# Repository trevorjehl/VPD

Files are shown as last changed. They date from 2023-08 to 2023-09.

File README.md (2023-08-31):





Stanford SNF

# Low-Cost Open Source Vapor Phase Decomposition Scanner

This purpose of this project is to create a low-cost vapor phase decomposition droplet scanner for use in semiconductor research labs. 

Scanner_Running_gif

<!-- ## Table of Contents

| Sections      | Description  |
|---------------|--------------|
| [Introduction](#introduction) | - Low-Cost Open Source Vapor Phase Decomposition Scanner<br> - Project Purpose |
| [Rationale](#rationale) | |
| [Download & Installation](#download--installation) | - Download Methods<br> - Python Version<br> - Project Dependencies |
| [Command Line Usage](#command-line-usage) | - Generating G-Code Files<br> - Usage on Ender 3 3D Printer |
| [Modifying The Scan Routine](#modifying-the-scan-routine) | - Custom Scan Documentation<br> - Advanced Modifications<br> - Contribution Guidelines |
| [Project Goals & Next Steps](#project-goals--next-steps) | - Scan Base Redesign<br> - Wafer Piece Scanning<br> - Increasing Scan Droplet Volume<br> - Enclosure Design<br> - Construction & Replication Instructions |
| [Credits](#credits) | - Collaborators<br> - Supervision |
| [License](#license) | - GPL v3 Licensing Information | -->

## Rationale

Although traditional semiconductor manufactureres have access to the large, expensive VPD machines to evaluate silicon wafer contamination, these machines can be innacesible for smaller research facilities.

This project uses a modififed low-cost, open source 3D-printer as the basic platform for the scanner. A custom printehead was designed to hold a 1mL acid-resistant (polypropylene) plastic syringe. This repo contains the neccesary code to program complex scanning sequences for the scanning apparatus.

## Download & Installation

To download the project, copy all project files to your hard drive. This can be done either by downloading the project, cloning the repo, or creating a branch.

- This project runs on Python 3.11.4, so ensure your Python installation is up to date.
- The only dependency for this project is the `math` module.

## Command Line Usage
To create a new G-Code file, use the following command line syntax:

```console
foo@bar:~$ python3 TEMPLATE.py filename.gcode
```

This will create a `.gcode` file in your local directory according to the settings and steps outlined in TEMPLATE.py. To run this easily on the Ender 3 3D printer (or similar), two methods can be used. For testing, software such as Repetier Host can be used, which communicates with 3D Printers over USB.

For more permanent installation, the `.gcode` file can be copied over to the 3D printer's SD/microSD card, which can then be run using the 3D printer's interface

## Modifying The Scan Routine
Refer to [CUSTOM_SCAN.md](/Guides%20&%20Additional%20Documentation/CUSTOM_SCAN.md) for detailed documentation, including various wafer sizes, using cuevettes for dispensing/collecting fluid, changing the location of the cuevette, scan speed, etc.

This project was created with customization in mind, and is therefore easy to modify to suit your needs. For more in-depth changes, consult [USING_TEMPLATE.md](/Guides%20&%20Additional%20Documentation/USING_TEMPLATE.md). 

If you do make changes, please contribute per the standards outlined in [CONTRIBUTING.md](CONTRIBUTING.md). As a reminder, if you release the modified version to the public in some way, the GNU license agreement requires you to make the modified source code available to the program's users.

## Project Goals & Next Steps
- [ ] Complete redesign of scan base to be CNC machined from Teflon/PTFE
- [ ] Add wafer piece scanning functionality (vacuum chuck?).
- [ ] Consider methods of increasing scan droplet volume, as this may aid ICP-MS measurements.
- [ ] Design encolosure/spill area to contain the system and any acid that may spill during operation.
- [ ] Create detailed construction/replication instructions with photos for use in other fabs.

## Credits
This project was made in collaboration with Uriel Valencia. Overseen by [Alexander Denton](https://profiles.stanford.edu/alexander-denton), Stanford Nanofabrication Facility. 

## License

This program is free software: you can redistribute it and/or modify it under the terms of the GNU General Public License as published by the Free Software Foundation, either version 3 of the License, or (at your option) any later version.

For further details, see <https://www.gnu.org/licenses/>.

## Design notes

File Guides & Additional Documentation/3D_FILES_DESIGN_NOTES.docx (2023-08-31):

Uriel Valencia

Stanford Nano Facilities

30 August 2023

Vapor Phase Decomposition (VPD) Machine - Wafer & Cuvette Holder Base, Wafer Holders, and Cuvette Holders

Wafer & Cuvette Holder Base (Original Design - 8/13/23):

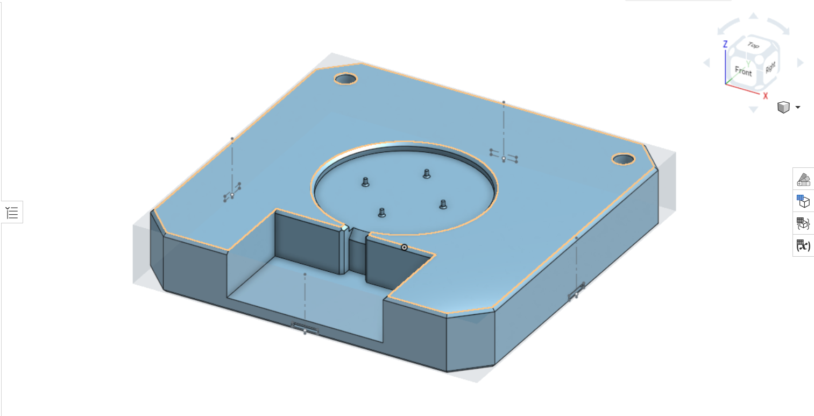
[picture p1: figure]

Figure 1: Wafer & Cuvette Holder Base (Original Design)

The original design for the Wafer & Cuvette Holder Base (to be referred to as “The Base”, from now on) was designed by taking measurements of a Cuvette, a 4” (100 mm) Silicon Wafer, Binder Clips, the bed of an Ender 3 3D Printer, and Wafer Tweezers. Rulers, as well as Calipers, were used to take measurements (in mm).

- The dimensions of The Base were determined by taking the height of a cuvette (40 mm), as well as the length and width of the Ender 3 3D Printer Bed (235 mm x 235 mm). The height of The Base was 38.6 mm, and the length and width were 225 mm x 225 mm after making some adjustments.
- Slots for binder clips were positioned on the Front, Left, Back, and Right sides of The Base. The dimensions for the slots were determined by taking measurements of the binder clips. The dimensions of the binder clip slots were 3 mm high x 16.5 mm wide x 3 mm wide.
- Two cuvette slots were made on the Top face of The Base. The height and diameter of the cuvette slots were determined by taking measurements of a cuvette. The dimensions of the cuvette slots were 38.6 mm deep, with a diameter of 11.5 mm.
- A slot for 4” silicon wafers was made on the Top face of The Base. The diameter of the wafer slot was erroneously determined by assuming that a 4” silicon wafer had a diameter of 101.6 mm. The diameter of the wafer slot was 102.1 mm. Four pegs were included on the bottom of the wafer slot to prevent either side of a silicon wafer from coming in full contact with The Base. The depth of the wafer slot was 5 mm, and the height of the pegs were 4 mm so that, when the silicon wafer was resting on the pegs, the surface of the silicon wafer would be flush with the Top face of The Base.
- A big cut out was placed on the Front face of The Base so that a hand could move with ease when handing wafer tweezers. There is another slot between the big cut out and the wafer slot. The width of the tweezer slot was determined by measuring the width of a wafer tweezer, 12.7 mm wide. The width of the tweezer slot was 14 mm wide. The tweezer slot was made so that any user could place or remove a 4” silicon wafer on the wafer slot.

The following sections will mention what did not work in the original design, the following versions, and what was done to improve on what did not work.

Wafer & Cuvette Holder Base (Original Design - V2 - 8/17/23)

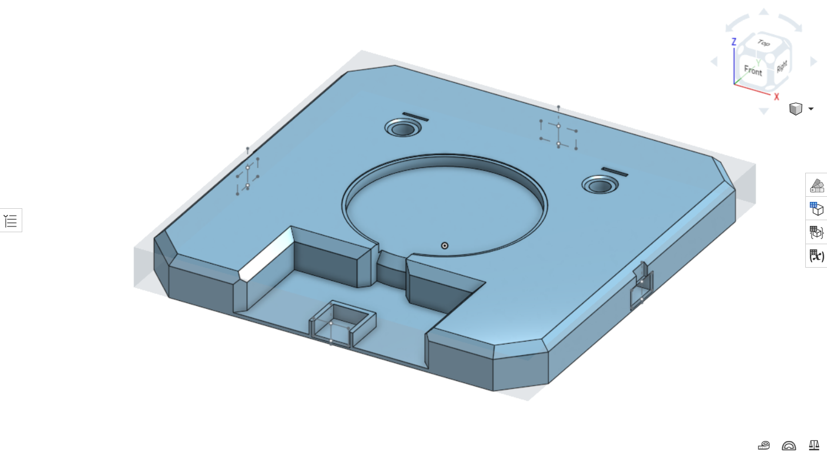
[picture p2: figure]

Figure 2: Wafer & Cuvette Holder Base (Version 2)

- The original design of The Base was too bulky. The length and width dimensions remained the same, but the height was reduced to 23 mm.
- The binder clip slots were not functional; the binder clips could not go into the slot. To fix the problem, the dimensions of the binder clips slots were changed to: 10 mm high x 20 mm wide x 20 mm long. This gave the binder clips enough clearance to go into the binder clip slots. An additional was made above the binder clip slots so that the handles of the binder clips could rest on them so the handles would not interfere with the bed of the Ender 3 3D printer when it moves in the y- direction.
- The two cuvette slots where the cuvettes would be placed in were too snug; force was needed to put in, and remove, the cuvettes from the circular slots. To fix this, the diameter was increased to 11 mm. The depth changed to 23 mm since the height of The Base was reduced to 23 mm. Additionally, there was an issue with repeatability; there was no way to prevent the cuvettes from moving in a circular motion while in the cuvette slots. To prevent the cuvettes from moving, slots for the caps of the cuvettes were made near the cuvette slots to hold the cuvettes in place. The dimensions of the cap slots were 1.6 mm long x 14 mm wide x 23 mm deep.
- The diameter of the wafer slot was too big. The diameter of the wafer slot was reduced to 101.86 mm. Also, the silicon wafer was not stable when placed on the pegs. Applying force to certain areas, like closer to the edge of the silicon wafer, would cause the silicon wafer to tilt. To fix this, the pegs were removed, and a ring that was 1mm lower than the wafer slot was used instead. The wafer ring was 98 mm in diameter.
- The wafer tweezer slot was too narrow; there was no room for the wafer tweezers to move sideways when placing or removing a silicon wafer. To fix this, the width of the wafer tweezer slot was increased to 20 mm.

Wafer & Cuvette Holder Base (Original Design - V3 - 8/18/23)

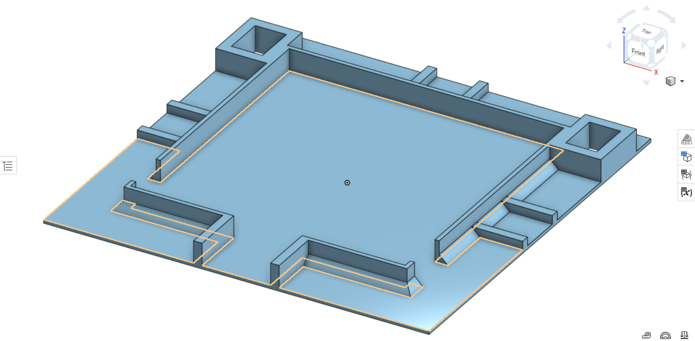
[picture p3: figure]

Figure 3: Wafer & Cuvette Holder Base (Version 3)

In this version of The Base, the wafer slot holder was removed. Since silicon wafers come in different diameters, 51 mm, 100 mm, and 150 mm, it was decided that a larger, rectangular slot, should be made so that three different wafer holders could be made, and therefore interchangeable. Also, the cuvette slots were removed, as well as the cap slots, in favor of cuvette holder slots, where cuvette holders could be inserted into the slots.

- The length and base of The Base remained the same. However, the height was reduced to 15 mm, but this was not applied to the entirety of The Base. The walls of the new wafer holder slots, as well as the cuvette holder slots, were elevated 13 mm high from the base, which was elevated 2 mm high.
- The width of the binder clip slots was increased to 25 mm. The length was increased to 29.85 mm so that the walls on either side of the binder clip slots would act as support for the walls of the wafer holder slot. The walls on either side of the binder clip slots were 5 mm wide, with a height of 5 mm.
- The cuvette slots, and cap slots, were removed and replaced with cuvette holder slots (cuvette holder slots will be talked about later). The external perimeter dimensions of the cuvette holder slots were 35.85 mm long, 29.85 mm wide, and 13 mm high. The internal perimeter dimensions of the cuvette holder slot were 24.2 mm wide, 18.2 mm wide, and 15 mm deep.
- The wafer slot was replaced with the wafer holder slot. The external perimeter dimensions of the wafer holder slot were 165.3 mm long and wide, with a height of 13 mm. The internal perimeter dimensions of the wafer holder slot were 160.3 mm long and wide, with a depth of 15 mm. Wafer holders will be talked about later.
- The big cut out from Version 1, and the wafer tweezer slot, became one. The new wafer tweezer slot was 40 mm wide and 29.85 mm long. The walls next to the wafer tweezer slot were 5 mm wide, 29.85 mm long, and 13 mm high.
- Cut outs were made on the Left and Right faces of the wafer holder slot. The cut outs were 8 mm long, 25 mm wide, and 13 mm high.

Wafer & Cuvette Holder Base (Final Version - 8/29/23)

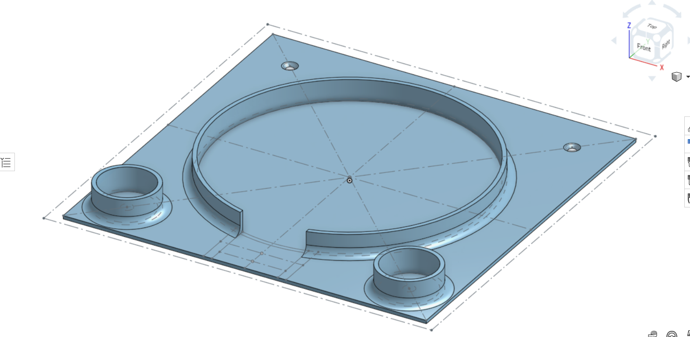
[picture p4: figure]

Figure 4: Wafer & Cuvette Holder Base (Final Version)

For the Final Version, the binder clip slots from previous iterations were removed, and instead replaced with holes so that The Base would be bolted on to the bed of the Ender 3 3D Printer. Also, the wafer holder slot, and the cuvette holder slots, were redesigned to be round, as opposed to square or rectangular. This design is better for when The Base gets manufactured.

- The length and width of The Base was reduced to 220 mm x 220 mm. This was done so that the length and width of The Base was within the effective printing area of the Ender 3D printer. Overall height of The base is 15 mm. The base is 2mm high, and the height of the wafer and cuvette holder slots are 13mm high.
- The binder clip slots were removed in favor of counter sink, standard M4 holes. The advantage to the counter sink holes is that the screws of the levels (on the bottom of the Ender 3 3D Printer bed) can be used to fasten the The Base onto the Ender 3D Printer bed.
- The previous cuvette holder slots were redesigned to be round. Easier to manufacture. The cuvette holder slots were moved from the back of the Top face to the front. Also, the two cuvette holder slots are located where two of the counter sink holes are located; the counter sink holes will not interfere with the cuvette holders.
- The wafer holder slot was redesigned to be round; easier to manufacture. The cut outs to remove the interchangeable wafer holders were removed. Instead, the cut outs were made on the bottom of the wafer holder, which can be accessed from the wafer tweezer slot.
- The walls next to the wafer tweezer slot area were removed, as they were unnecessary at this point. The width of the wafer tweezer slot remained the same.

Rectangular Cuvette Holder (Original Version - ~ 8/15/23)

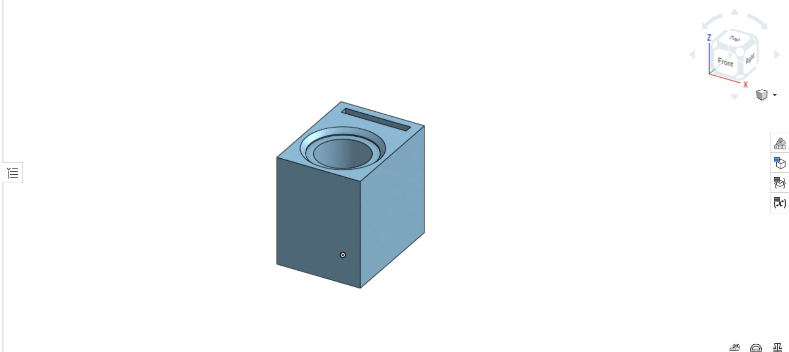
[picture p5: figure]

Figure 5: Rectangular Cuvette Holder (Original Design)

This Rectangular Cuvette Holder (to be referred as “The Cuvette Holder” from now on) was made during V3 of The Base was being designed.

- The cuvette Holder is 24 mm long x 18 mm wide, with a height of 23 mm. The height of The Cuvette Holder was intentionally higher than the cuvette holder slot on The Base so that The Cuvette Holder could be easily placed and removed.
- The diameter of the slot where the cuvette goes in is 11 mm, and it is 23 mm deep (from Top face to the Bottom face. The cap slot is 1.7 mm long and 14 mm wide, with a depth of 23 mm.
- The lip of the cuvette does not rest on the Top face of The Cuvette Holder. The Cuvette Holder is intentionally shorter than the cuvette so that the cuvette can be easily placed and removed from the cuvette slot.

Round Cuvette Holder (Final Version - 8/29/23)

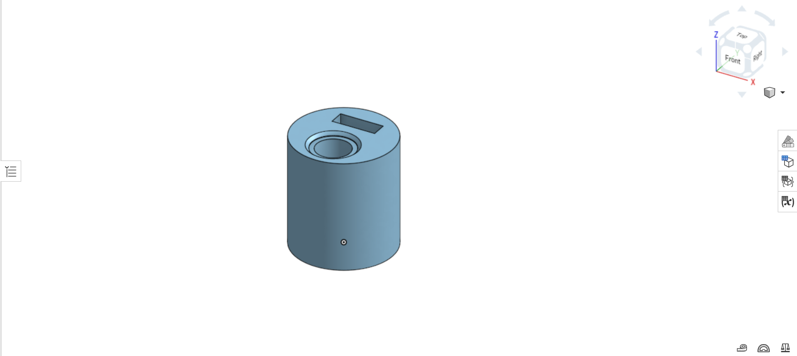
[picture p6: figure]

Figure 6: Round Cuvette Holder (Final Version)

The (Round) Cuvette Holder was made when the Final Version of The Base was being designed.

- The Cuvette Holder was redesigned to be round so it would fit in the circular cuvette holder slots in the Final Version of The Base. The diameter of The Cuvette Holder is 32 mm, and its height was increased to 35 mm so that the cuvette would have less room to move around.
- The diameter of the cuvette slot was reduced to 10.9 mm so that the cuvette would move around less. The depth of both the cuvette slot, and the cap slot, was increased to 35 mm. The length of the cap slot was increased to 4.9 mm so that more of the cap would fit in the slot.

Wafer Holder (Original Version - 8/21/23)

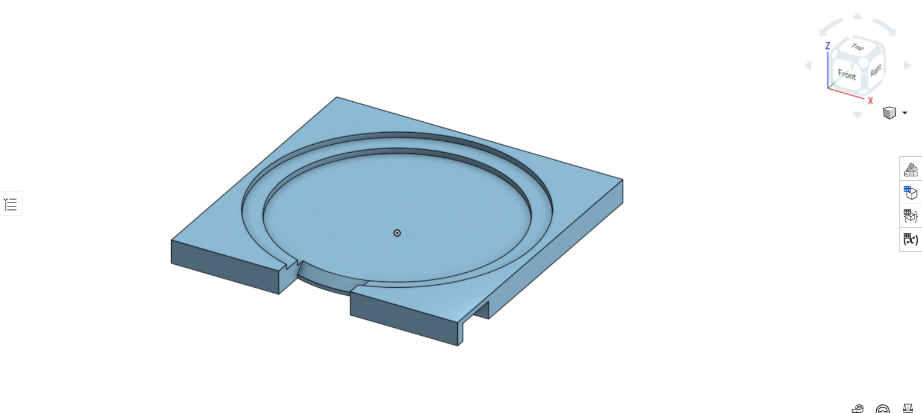
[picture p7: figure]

Figure 7: 6” Wafer Holder (Original Version)

The Wafer Holders (of sizes 51 mm, 100 mm, and 150 mm) were designed when V3 of The Base was being designed. The idea was to create three separate wafer holders, for each size of silicon wafer, so that they could be interchangeable with V3 of The Base.

- The dimensions of the wafer holder (for all three sizes) were 160 mm long x 160 mm wide, with a height of 13 mm.
- The difference between the three wafer holders are the diameters of the wafer slots, as well as the wafer rings the silicon wafers rest on. The 6” Wafer Holder (Figure 7) has a wafer slot diameter of 150.6 mm, and a wafer ring diameter of 130 mm. For the 4” Wafer Holder, the wafer slot diameter was 100.6 mm, with a wafer ring diameter of 80 mm. For the 2” Wafer Holder, the wafer slot diameter was 51.6 mm,and the wafer ring diameter was 30 mm.
- The wafer tweezer slot remained the same; 40 mm wide.
- Slots to remove and place the wafer holder from The Base were placed on the Left and Right faces of the wafer holders. The slots were 20 mm long by 25 mm wide, with a height of 10 mm.

Wafer Holder (Final version - 8/29/23)

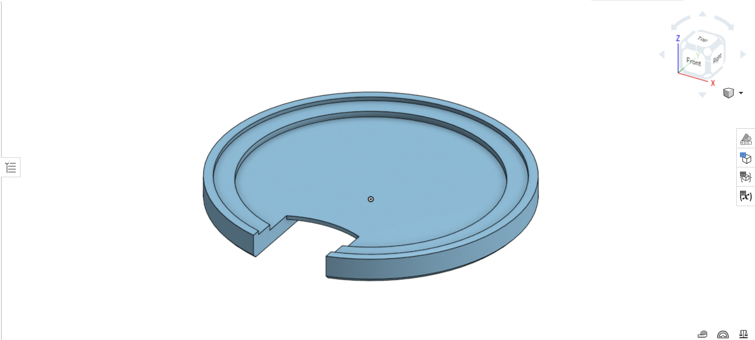
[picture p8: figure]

Figure 8: 6” Wafer Holder (Final Version)

The Final version of the wafer holders (51 mm, 100 mm, and 150 mm) were redesigned so that they would fit the Final Version of The Base.

- The wafer holders were redesigned to be circular so that they would fit the circular wafer slots of the Final Version of The Base. All three wafer holders had a diameter of 160 mm. Diameters for the wafer slots, as well as the wafer rings, remained the same.
- The width of the wafer tweezer slot remained unchanged.
- The slots to place and remove the wafer holders from The Base were removed from the, and instead a slot was created under the wafer tweezer slot. For all three wafer holders, the dimensions of the slot to place and remove the wafer holder are 25 mm long x 40 mm wide, with a height of 6 mm.

VPD Machine

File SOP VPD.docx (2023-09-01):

Document: Vapor Phase Decomposition Droplet Scanner Standard Operating Procedure | Revision: A | Release Date:

Prepared by: Trevor Jehl

Table of Contents

# 1. Equipment Purpose

  1.1. The VPD droplet scanner is designed to use an acidic scanning solution to extract contaminants from a silicon wafer so that the contaminants may later be measured through use of an ICP-MS.

# 2. Equipment Specifications

# 3. Cleanliness Standard

  3.1. TBD

# 4. Processing Capabilities

# 5. Becoming a User

# 6. Safety

  6.1. This device uses an acidic scanning solution that contains HF. Ensure that all proper protocols are followed for acid & HF handling. If the contact is made with HF, immediately stop using the machine follow the necessary procedure for an HF spill.
  6.2. This device has open, moving wires. Before use, ensure that all wires are free to move and that they will not cause damage when the machine is in motion.
  6.3. This machine has multiple cooling ducts and fan systems to ensure proper cooling of all electronic components.
    6.3.1. Ensure that each cooling duct is not blocked before using the machine.
    6.3.2. If liquid of any kind, including the scanning liquid, comes in contact with the metal frame of the machine, immediately turn off power to the machine and unplug it from all outlets. Ensure that the spill is properly reported and handled. Before resuming use, ensure that all electronic components are free from moisture and corrosion.
  6.4. During and following use, the machine’s motors will become hot to the touch. Take precautions to ensure that this heat does not cause harm to the user or to lab equipment.

# 7. Required Equipment

  7.1. 4 or 6 inch silicon wafer. Wafer pieces are not able to be processed at this time.
  7.2. Appropriate size wafer holder for the wafer being scanned.
  7.3. Sanitized 1mL polypropylene plastic syringe.
  7.4. Sanitized cuvette for storage of sample droplet.
  7.5. Pre-mixed scanning solution.

# 8. Operating Procedure

Before beginning, familiarize yourself with the safety considerations outlined in section 6.

  8.1. If the scan head is not in the back left corner of the scan plate, follow abort procedure (section 13) to avoid damaging the machine.
  8.2. Perform an overall inspection of the machine. Ensure that all wires are free to move and will not catch during machine operation. Ensure that all air ducts are free from debris and moisture. Ensure that the scan motor cable is properly seated in the scan motor cable guide.
  8.3. Align the syringe plunger holder with the zero mark on the syringe, either by using the provided alignment mark on the side of the scan head or by inserting a syringe into the head, depressing the plunger holder as much as possible, and carefully removing the syringe to avoid moving the plunger holder.
  8.4. Find the correct size wafer holder for your sample and insert it into the scan base, making sure that the slot in the wafer holder aligns with the corresponding slot on the scan base. Carefully insert your wafer into the slot in the wafer holder.
  8.5. Turn the machine on using the red switch on the right side of the machine. Depress the selection wheel to access the menu items. Rotate the wheel to select “Print from Media.” Depress the wheel again to select.
  8.6. Rotate the selection wheel to find the appropriate scan routine for your wafer (e.g. for a 4 inch wafer, select “4inScan.gcode”). Depress the wheel and select “Print” to begin the scan.
  8.7. After automatic calibration, the scanner will place the scan head over the wafer, open the plunger holder, and beep. Fill your sanitized syringe with the appropriate amount of scan solution (see section 11), and place it into the slot in the scan head, making sure that the plunger is securely seated in the plunger holder. Once finished, depress the selection dial to begin your scan.
  8.8. The scanner will begin the scan routine. At the end of the cycle, it will collect the scan droplet, fully open the syringe plunger holder for easy removal, and emit an audible beep.
  8.9. Once the cycle has finished and the scanner has beeped, remove the syringe from the plunger, making sure not to spill any solution from the syringe. Dispense your sample into the appropriate cuvette and seal it. Press the selection dial once more to finish the cycle. Dispose of the syringe appropriately.
  8.10. Depress the selection dial, which will move the plunger holder to the “0” mark and move to the scan head to the back left of the scan plate. Turn the machine off using the red switch on the right side of the machine.
  8.11. Remove the wafer with wafer with wafer tweezers.
  8.12. If any solution spilled during the procedure, clean all affected parts thoroughly.
9. Recipe Parameters
  9.1. Scan Solution:

# 10. Definitions and Process Terminology

  10.1. Bed Leveling Knobs: The bed leveling knobs are positioned at the four corners of the scan plate. They serve to adjust the compression of the scan plate spacers.
  10.2. Cuvette Holder: Small, cylindrical plastic piece that can be inserted into the scan base. The cuvette holder has a hole through its center so that the cuvette may be inserted into it.
  10.3. Cuvette: A clear plastic container for holding the scan droplet.
  10.4. End Stop: Physical switches on the X & Y axes that tell the system where the ends of the
  10.5. ICP-MS: Inductively coupled plasma mass spectrometry. The technique used to quantify the composition of contaminants in the scan droplet.
  10.6. Interface Screen: The LCD panel at the bottom right of the machine. Used to interact with the machine and select a scanning protocol.
  10.7. Pinion Gear: The plastic gear mounted to the front side of the scan head. It is responsible for transferring the rotational motion of the scan motor to the plunger holder.
  10.8. Plunger Holder: The long, sliding plastic component that wraps around the end of the syringe’s plunger so that it may be moved up and down via the pinion gear and scan motor.
  10.9. Scan Base: The large plastic piece that is mounted to the scan plate and has cylindrical holes for the cuvette holders(s) and wafer holder.
  10.10. Scan Droplet: The small volume of scan solution dragged by the syringe which dissolves and collects wafer contaminants.
  10.11. Scan Head: The plastic assembly bolted to the x-axis gantry. The scan head is connected to the syringe, plunger holder, scan motor, and pinion gear.
  10.12. Scan Motor Wire Guide: This white plastic guide is attached to the top Delrin roller wheel on the left side of the x-axis gantry. It ensures that the scan motor does not become tangled, caught, or otherwise damaged as the scan head moves.
  10.13. Scan Motor: The silver and black rectangular prism bolted into the scan head. This motor is responsible for moving the syringe’s plunger by moving the pinion gear.
  10.14. Scan Plate Spacers: Four cylinders with holes through their center points for countersunk bolts. These spacers keep the scan plate even and level across it’s face.
  10.15. Scan Plate: The large square metal base that the scan base is bolted to.
  10.16. Scan Solution: The acidic solution that makes up the scan droplet. This solution is used to dissolve contaminants in the wafer.
  10.17. Selection Dial: The round knob at the bottom right below the interface screen.
  10.18. Syringe: This system is designed to use 1mL HSW® Norm-Ject® Luer-Slip Syringes, Air-Tite. This syringe press fits into the scan head, and the syringe plunger fits into the plunger holder. They can be easily identified by their blue-green plunger and clear main body.
  10.19. VPD: Vapor phase decomposition, an established technique for contamination analysis of wafers.
  10.20. Wafer Holder: Cylindrical insert for the scan plate upon which the silicon wafer to be scanned rests.

# 11. Process Data

  11.1. 4-inch (100mm) Wafer
    11.1.1. Scan Duration: ~20 minutes.
    11.1.2. Scan Radius: From radius 65.0mm to 5.0mm
    11.1.3. Scan Droplet Volume: 0.05mL
  11.2. 6-inch (150mm) Wafer
    11.2.1. Scan Duration: ~53 minutes.
    11.2.2. Scan Area: From radius 40.0 to 4.0.
    11.2.3. Scan Droplet Volume: 0.05mL

# 12. Troubleshooting

Symptom | Issue | Resolution
The loaded syringe won’t fit into the scan head. | Failure to align the plunger holder before scan. | Turn the machine off. Align the mark on the plunger holder with the mark on the scan head body. Alternatively, place the syringe with the plunger fully depressed into the scan head. Once the plunger is fully aligned at 0mL, remove the syringe. Be careful not to move the plunger holder.
The printer won’t move after starting a scan routine or after instructing printer to move | Disconnected wires | Ensure that all four (4) motor wires are fully connected. Ensure that all three (3) end stop cables are fully connected. Cables are labeled for convenience with yellow tags at the cable ends.
There are no files under “Print from Media” | SD read error or disconnected SD card | Above “Print from Media,” press “Change Media” to re-read the SD card. Recheck “Print from Media.” If there are still no visible files, turn off the scanner. Unplug the microSD card from the front of the scanner, remove it, and replace it. Ensure that it fully ‘clicks’ in. Recheck “Print from Media.”
The scan droplet is consistently lost in the same spot on the wafer | Uneven scan surface. | First, ensure that the wafer holder is fully seated and flat in the scan base. Verify that the syringe is fully seated in the scan head. If problems persist, verify the adjustment of the eccentric nuts, particularly on the scan head and y-axis. If issues continue, level the system by following the leveling procedure outlines in “Maintenance”
The system won’t turn on. | Loose power cable. | Over time, the power cable can become loose. Make sure the red switch is set to off (O) before checking that both the system side and wall socke side of the power cable is fully seated.

# 13. Abort Procedure

If, for any reason, the machine must be interrupted during a regular scan cycle, follow this procedure to prevent damage to the system.

  13.1. Turn the machine off using the red power switch on the right side of the machine. Then, unplug the power cord.
  13.2. Clean up any scanning solution that may be left behind. Remove the syringe from the scan head.
  13.3. Move the syringe plunger holder down to the zero point. You will be unable to do this after the machine is powered on.
  13.4. Once the system has been cleaned, ensure that the red switch is in the OFF (O) position before plugging in the power cable. Once the cable is fully seated, you may turn the system on.
  13.5. Finally, it is important to ensure that the printhead will not encounter any obstacles when running the next scan procedure. To do so, use the machine’s interface (Press knob > Motion > Move Axis > Move Z > Move 10mm > Rotate knob to move) to raise the Z-axis well above any obstacles on the XY plane.

# 14. Maintenance

To ensure smooth operation of the system, a few regular maintenance items should be conducted. This section will divide these maintenance items by the frequency that they should be performed.

Before performing any maintenance, ensure that the machine has been turned off and is unplugged unless otherwise noted.

  14.1. XY Belts
    14.1.1. Belt Tension: The X & Y belts of the system help maintain the dimensional consistency of the scanner. Over time, these belts will loosen and the machine’s ability to move in the XY plane will be hampered. To tighten the belts
      14.1.1.1. Locate and access the belt tensioner at one end of the axis on which you want to tighten the belt.
      14.1.1.2. Use the appropriate Allen key to loosen the belt tensioner. There are two screws on the X-axis and four on the Y-axis of the machine.
      14.1.1.3. Once the tensioner is loose on the frame, hold the frame with one hand and with moderate strength pull the tensioner in the direction that will tighten the belts (away from the moving part).
      14.1.1.4. Hold the tensioner in its far-back position, let go of the frame, and, using the Allen key used earlier, tighten the bolts so that the tensioner is tight. Do not overtighten these bolts.
      14.1.1.5. After tensioning the system, perform a visual inspection of the T-nuts behind the bolts. Ensure that they are facing upwards, perpendicular to the length of the metal frame. If they are not, the nut will not be secured against the frame and the belt will quietly lose tension. See (15.2) for a visual guide to proper installation.
    14.1.2. Belts are a consumable part. After extended periods of use, they will show signs of wear (cracking, tearing, fraying). Replace and reattach belts as needed. Follow the above procedure to ensure proper belt tension.
  14.2. Delrin V-Slot Wheels
    14.2.1. The moving axes of this printer connect to the frame via rolling Delrin wheels.
      14.2.1.1. Each side of the x-axis gantry has three (3) wheels. The scan head has another three (3) wheels. Below the moving y-axis plate are four (4) additional wheels.
    14.2.2. If scan head wobble, grinding, skipping, excess wear, inaccurate XY motion (after ensuring proper belt tension) Wheel tightness to the frame can be adjusted using the eccentric nuts on the machine. Each side of the x-axis gantry has one (1) eccentric nut on the inside rolling wheel. The scan head has one (1) nut on the bottom wheel. The right side of the rolling y-axis gantry has two (2) eccentric nuts. These nuts can be identified by their larger size and hexagonal shape. See (15.1) for a photo example. To adjust the nuts:
      14.2.2.1. Obtain the proper size wrench (10mm).
      14.2.2.2. Identify the axis and eccentric nut that need to be adjusted.
      14.2.2.3. Using the wrench, rotate the nut. To check tightness, hold the axis in place and attempt to rotate the Delrin wheel. The wheel should rotate in place with a slight amount of force needed to keep the axis in place.
      14.2.2.4. Once you are satisfied with the ability of the wheel to rotate, check the other wheels of the axis as they will have been affected by this adjustment.
      14.2.2.5. Finally, verify overall axis motion. The axis should move freely without excess resistance but should be tight enough to be free of wobble, tilt, or rotation.
    14.2.3. These wheels are consumable and will wear over time. Symptoms of worn wheels include visible wear on axes and frame of printer, sagging x-axis gantry, inconsistent or inaccurate axis motion, or significant differences noted in the size or shape of one of the wheels. Before replacing wheels, ensure that the eccentric nuts have been adjusted properly.
  14.3. Z-Axis Threaded Rod
    14.3.1. The Z-axis threaded rod is located behind the left vertical frame of the machine. It is responsible for powering the vertical movement of the scan head.
    14.3.2. Since the rod has metal-on-metal contact, it will require periodic lubrication to prevent excess wear. To lubricate the axis:
      14.3.2.1. Remove any old lubricant by thoroughly cleaning the rod using isopropyl alcohol. Use the machine’s controls (Press knob > Motion > Move Axis > Move Z > Move 10mm > Rotate knob to move) to spin and move the axis for thorough cleaning. Be careful not to raise the Z-axis too high to prevent snagging or catching of wires.
      14.3.2.2. Apply an appropriate amount of lubricant to the length of the rod. Use the machine again to move the axis up and down multiple times to ensure even distribution across the rod.
      14.3.2.3. If using non-Teflon lubricant, wipe off excess lubricant to leave behind only a thin layer.
  14.4. Scan Plate & Scan Plate Springs
    14.4.1. Currently, the system uses springs to level the scan plate, which in turn levels the scan bed, the wafer holder and wafer. Ensuring that the scan plate is level relative to the syringe tip is essential for reliable operation of the system. If the plate is not level, the distance from the syringe tip to the wafer will vary across the scan, and the tip may lose contact with the drop or dig into the wafer or wafer holder. To level the scan plate:

(Note: Be advised that if the bed is particularly poorly leveled at the start of this process, the syringe tip may grind and press into the wafer holder plate. If there is concern that this may be an issue, tighten all four (4) knobs down before beginning the scanning process).

      14.4.1.1. Obtain either a 0.1mm feeler gauge or a blank piece of printer paper. You will also need a syringe and the 4in wafer holder. Insert the wafer holder into the scan base.
      14.4.1.2. Navigate to the “Print from media” menu on the scanner and select “levelScanner.gcode” The scanner will automatically calibrate before moving to the center of the wafer holder. After the beep, insert the syringe and press the selection dial to begin the leveling process.
      14.4.1.3. The syringe tip will lower down to Z = 0. In sequence, the syringe tip will be slowly moved towards the four corners of the scan plate. The user will level each point, then the system will return to each point to check that the level was executed properly.
      14.4.1.4. To level a point, slide the feeler gauge or portion of paper underneath the tip of the syringe. Adjust the respective leveling knob so that there is a slight amount of resistance when moving the gauge or paper. Remember that that when looking straight down over the scanner, rotating the knobs clockwise will tighten them, increasing the gap between the syringe and surface. To decrease the distance, turn the knobs counterclockwise.
      14.4.1.5. Once you are satisfied with the point, press the selection knob to move to the next point.
      14.4.1.6. After you have leveled and re-leveled all four points, the scan holder will open the plunger for easy removal of the syringe. Remove the syringe and press the selection knob. Your leveling is now complete.
  14.5. Scan Head (Syringe Holder, Plunger Holder, Pinion Gear, Scan Motor)
    14.5.1. The plunger holder should not need regular maintenance or replacement.
    14.5.2. Periodically check the rack gears on the plunger holder for degradation with use. If wear is noted, replace with a new plunger holder.
    14.5.3. The pinion gear may wear with time. If any wear is noted, remove the gear, and replace with a new gear. To check for wear:
      14.5.3.1. Remove the syringe plunger holder and inspect the gear teeth. They should be straight, with no crushing, warping, twists, or other defects.
      14.5.3.2. To check the connection between the pinion gear and scan motor, run a scan cycle. Observe the interface between shaft of the scan motor and the pinion gear. If there is slipping between the two surfaces, the gear is worn and should be replaced.
    14.5.4. Periodically check all screws and bolts for proper fit and tightness. If bolts are loose, tighten them to finger tightness. Do not over tighten.
    14.5.5. Periodically check the scan motor cable for wear, with particular emphasis on the bottom portion of the cable, as it comes in contact with the scan motor wire holder during scanning. Replace as needed.

# 15. Appendices, Figures & Schematics

  15.1. Y-Axis Eccentric Nut

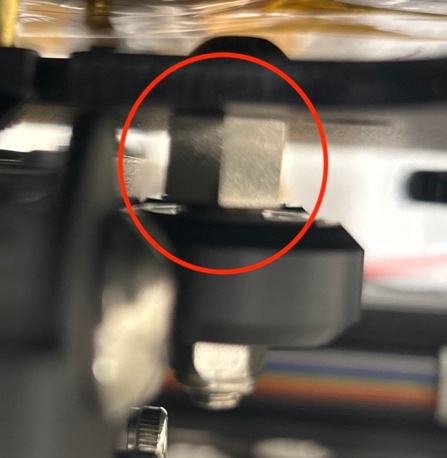
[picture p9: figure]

  15.2. T-Nut Proper & Improper Installation
    15.2.1. Proper T-Nut Installation

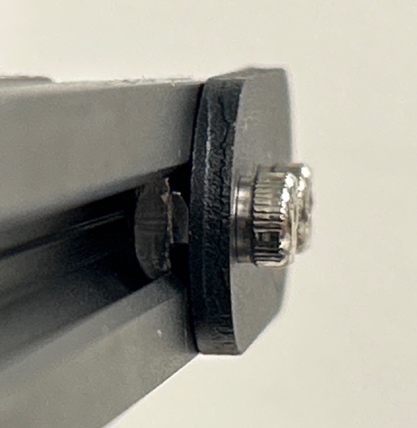
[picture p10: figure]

    15.2.2. Improper T-Nut Installation

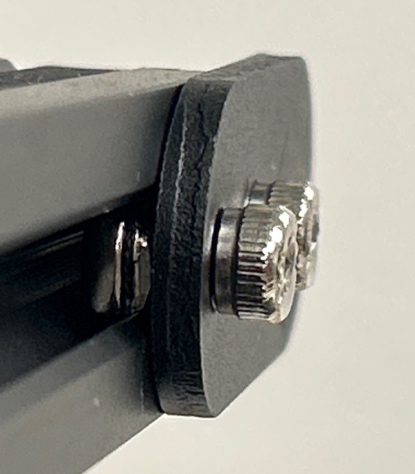
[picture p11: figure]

# 16. Revision Block

Revision | Date | Description of Change | Author
1 | 8/31/23 | Initial creation of SOP. | Trevor Jehl

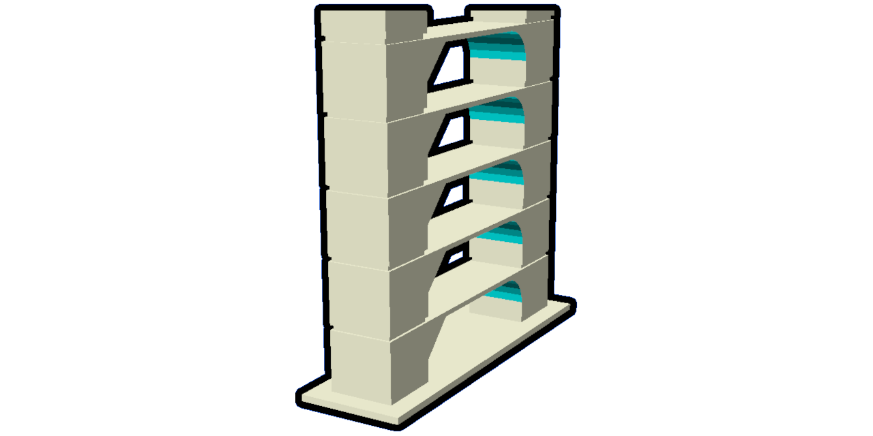
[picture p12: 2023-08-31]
Ender 5 Cura Config/5.4/plugins/AutoTowersGenerator/AutoTowersGenerator/Resources/Images/github_image.png

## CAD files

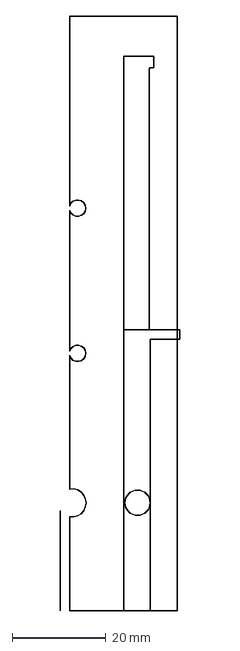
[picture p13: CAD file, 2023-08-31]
CAD FIles/3mL Plastic Syringe Head v15/Syringe Head 1_f84ff1b6/Syringe Holder 1_7d3c671d/Main Syringe Revolve.dxf
25.5 x 127.0 mm

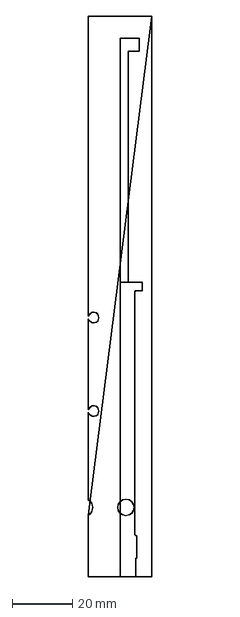
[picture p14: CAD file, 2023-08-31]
CAD FIles/Depracated/7.10.23(morePrintable) v3/Syringe Holder 1_7d3c671d/Main Syringe Revolve.dxf
20.9 x 186.0 mm

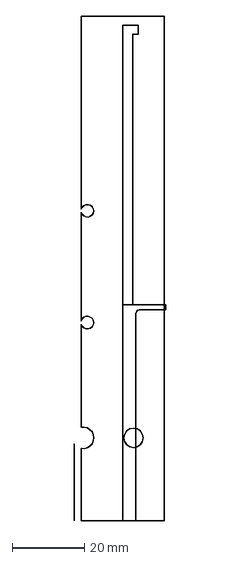
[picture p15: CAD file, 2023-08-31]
CAD FIles/1mL Plastic Syringe Head v13/Syringe Head 1_f84ff1b6/Syringe Holder 1_7d3c671d/Main Syringe Revolve.dxf
25.5 x 140.0 mm

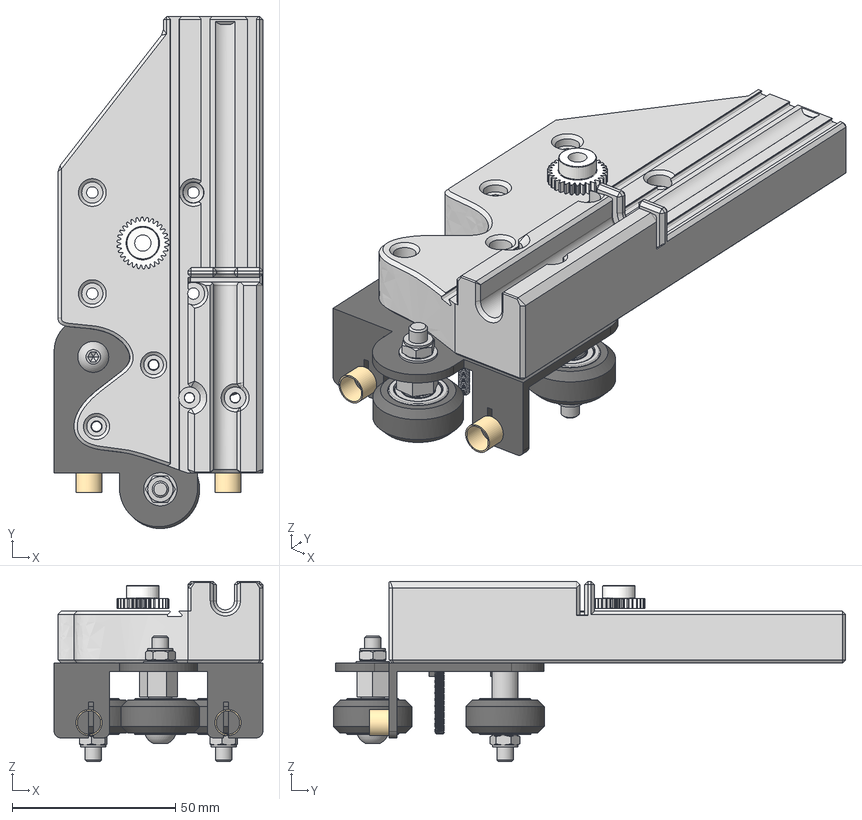
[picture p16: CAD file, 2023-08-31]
CAD FIles/1mL Plastic Syringe Head v13/1mL Plastic Syringe Head_v13.step
64.1 x 157.1 x 55.3 mm
M5X30 Pan Head Screw x 3
M5 Self-locking nut x 3
Rollers x 3
M5 washer1 x 3
625pillow x 6
Eccentric column
M5 washer
Spacers for rollers x 2
Copper Covers x 2
Metal Mounting Bracket
Syringe Holder
20 Degree Pressure Angle Plastic Gear v1 (1)
92095A185_Button Head Hex Drive Screw

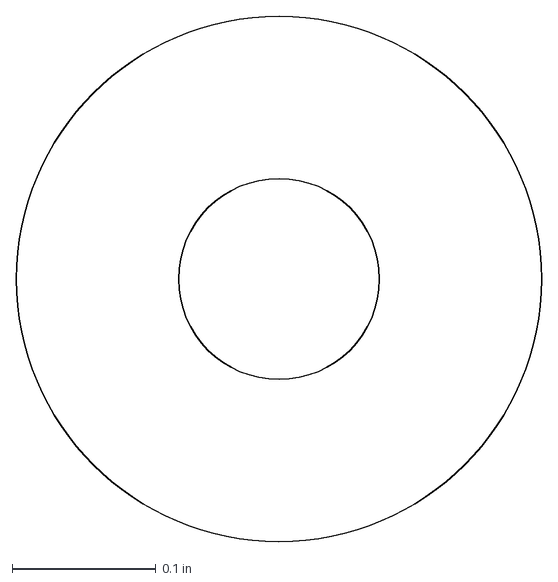
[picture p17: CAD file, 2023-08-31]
CAD FIles/1mL Plastic Syringe Head v13/Syringe Head 1_f84ff1b6/1mL Glass Syringe v18 1_c14a9fbb/Plunger 1_b5b81f4f/Sketch1.dxf
0.366 x 0.366 in

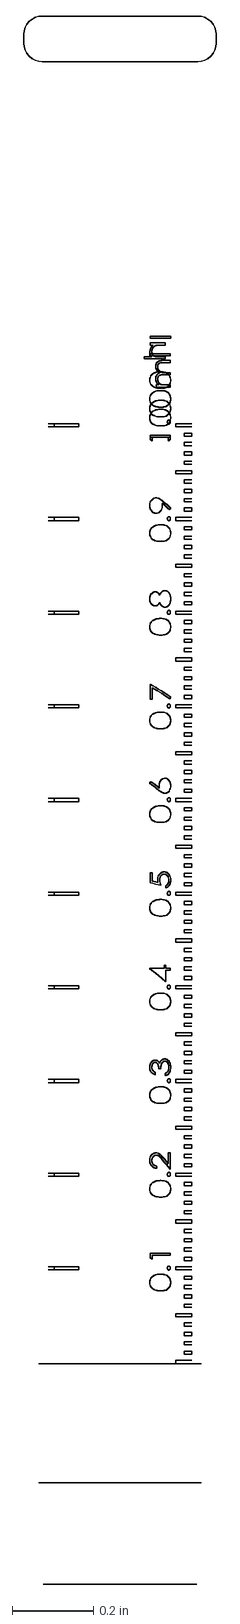
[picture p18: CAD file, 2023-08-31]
CAD FIles/1mL Plastic Syringe Head v13/Syringe Head 1_f84ff1b6/1mL Glass Syringe v18 1_c14a9fbb/Sketch1.dxf
0.472 x 3.85 in

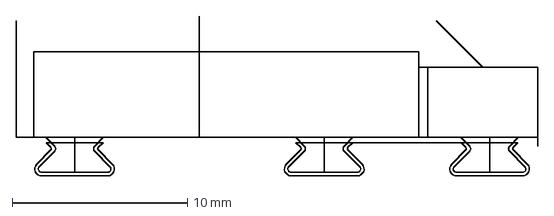
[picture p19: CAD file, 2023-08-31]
CAD FIles/1mL Plastic Syringe Head v13/Syringe Head 1_f84ff1b6/Plunger Holder 1_a4f4313b/Plunger Holder Tracks.dxf
29.8 x 9.14 mm

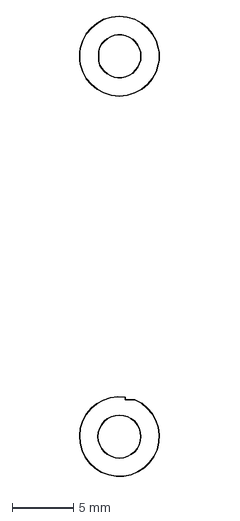
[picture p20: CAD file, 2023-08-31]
CAD FIles/1mL Plastic Syringe Head v13/Syringe Head 1_f84ff1b6/Syringe Holder 1_7d3c671d/Sketch7.dxf
7.17 x 37.8 mm

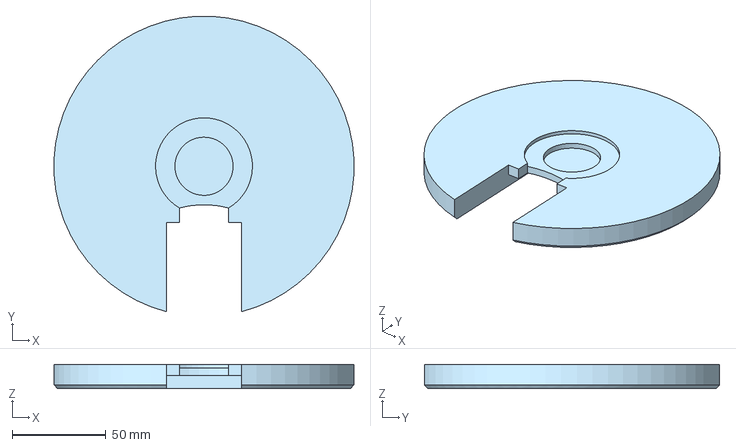
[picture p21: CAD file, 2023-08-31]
CAD FIles/2_ Wafer Holder/[Final] 2_ Wafer Holder (W- Tolerance, 8-29-23).step
159.8 x 157.3 x 13.0 mm

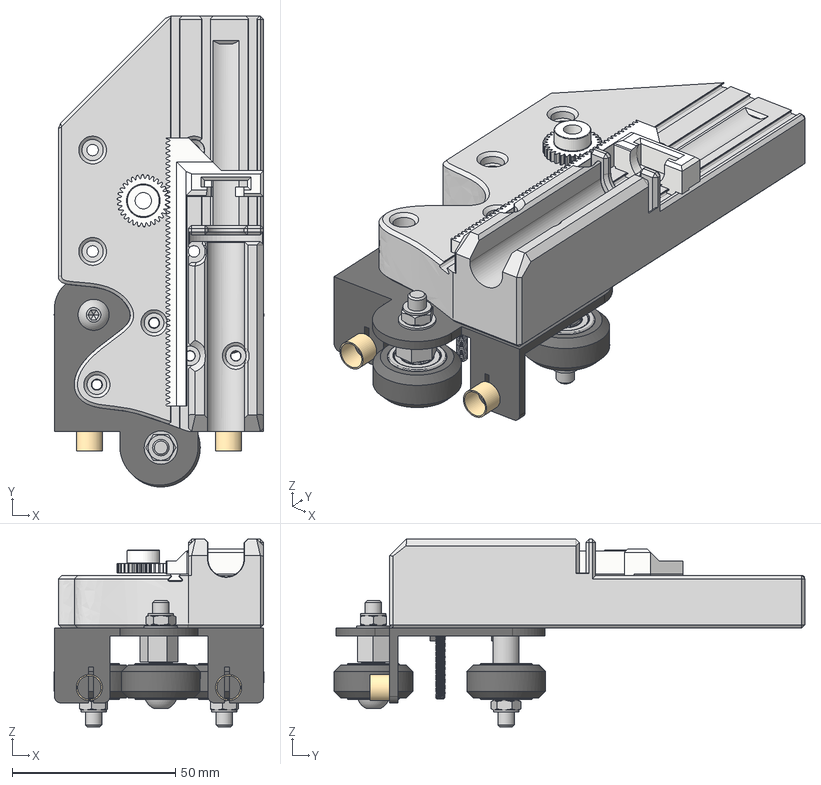
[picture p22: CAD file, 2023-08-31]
CAD FIles/3mL Plastic Syringe Head v15/3mL Plastic Syringe Head_v15.step
64.1 x 144.1 x 57.4 mm
M5X30 Pan Head Screw x 3
M5 Self-locking nut x 3
Rollers x 3
M5 washer1 x 3
625pillow x 6
Eccentric column
M5 washer
Spacers for rollers x 2
Copper Covers x 2
Metal Mounting Bracket
Syringe Holder
20 Degree Pressure Angle Gear Rack v1
20 Degree Pressure Angle Plastic Gear v1 (1)
92095A185_Button Head Hex Drive Screw

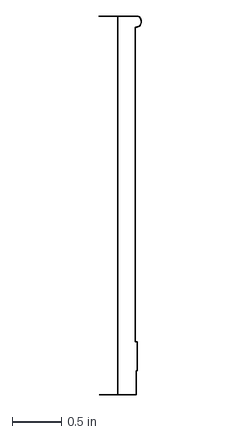
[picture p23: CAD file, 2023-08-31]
CAD FIles/3mL Plastic Syringe Head v15/Syringe Head 1_f84ff1b6/1mL Glass Syringe v18 1_c14a9fbb/Sketch3.dxf
0.427 x 3.85 in

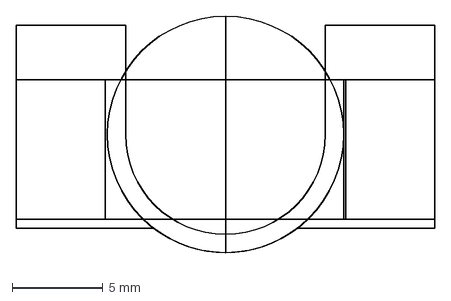
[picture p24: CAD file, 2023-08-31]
CAD FIles/3mL Plastic Syringe Head v15/Syringe Head 1_f84ff1b6/Plunger Holder 1_a4f4313b/Plunger Holder.dxf
23.0 x 13.4 mm

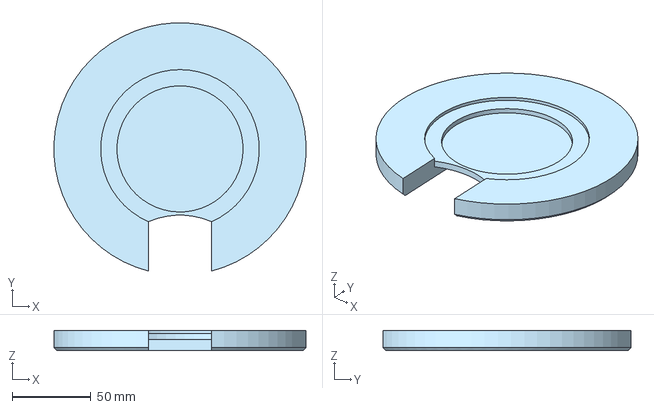
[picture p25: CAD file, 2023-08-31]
CAD FIles/4_ Wafer Holder/[Final] 4_ Wafer Holder (W- Tolerance, 8-29-23).step
159.8 x 157.3 x 13.0 mm

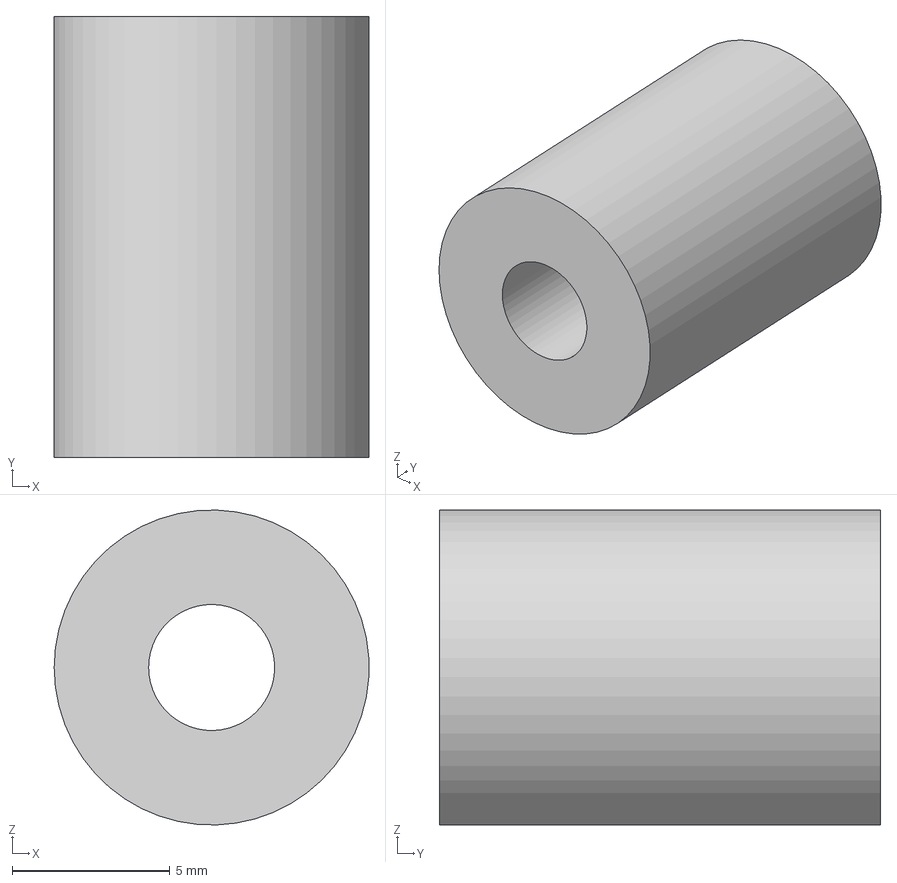
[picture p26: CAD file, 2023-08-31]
CAD FIles/bedSpacer v1/bedSpacer_v1.step
9.99 x 14.0 x 10.00 mm

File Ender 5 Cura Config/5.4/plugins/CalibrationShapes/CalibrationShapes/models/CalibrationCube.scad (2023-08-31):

// XYZ 20mm Calibration Cube
// Based on the design proposed by iDig3Dprinting https://www.thingiverse.com/thing:1278865
// Freely adapted by 5@xes

font = "Arial:style=Bold";

$fn=100;

cube_size = 20;
letter_size = 0.5*cube_size;
letter_height = 0.2*letter_size;

o = cube_size / 2 - letter_height / 2;

module letter(Txt) {
  color("Yellow")
  linear_extrude(height = letter_height) {
    text(Txt, size = letter_size, font = font, halign = "center", valign = "center");
  }
}

translate([0, 0, 10]) difference() {
  color("gray") 
  cube(cube_size, center = true);
  translate([0, -o, 0]) rotate([90, 0, 0]) letter("X");
  translate([o, 0, 0]) rotate([90, 0, 90]) letter("Y");
  translate([0, 0, o])  letter("Z");
}

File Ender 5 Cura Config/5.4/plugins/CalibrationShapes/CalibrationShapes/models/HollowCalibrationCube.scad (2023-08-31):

// XYZ 20mm Hollow Calibration Cube
// Based on the design proposed by iDig3Dprinting https://www.thingiverse.com/thing:1278865
// Freely adapted by 5@xes

font = "Arial:style=Bold";

$fn=100;

cube_size = 20;
letter_size = 0.5*cube_size;
letter_height = 0.2*letter_size;

o = cube_size / 2 - letter_height / 2;

module letter(Txt) {
  color("Yellow")
  linear_extrude(height = letter_height) {
    text(Txt, size = letter_size, font = font, halign = "center", valign = "center");
  }
}

translate([0, 0, 10]) difference() {
  color("gray") 
  cube(cube_size, center = true);
  translate([0, -o, 0]) rotate([90, 0, 0]) letter("X");
  translate([o, 0, 0]) rotate([90, 0, 90]) letter("Y");
  translate([0, 0, o])  letter("Z");
  cube((cube_size-letter_height), center = true);
}

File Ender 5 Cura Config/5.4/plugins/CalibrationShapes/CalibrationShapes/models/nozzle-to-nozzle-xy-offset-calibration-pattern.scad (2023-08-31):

/**
 *
 * Run:
 *
 *    openscad <file_name>.scad
 *    openscad [options] <file_name>.scad
 *
 * Options with -D <var=val>:
 * 
 *    teeth_count      number of teeth, recommended: 10 for positive offset + 10 for negative offset + 1 center = 21
 *    tooth_width      width of one single tooth
 *    tooth_height     height of teeth / comb, should be n * layer_height
 *    tooth_length     length of one single tooth
 *    teeth_gap        space in between teeth of the unscaled comb
 *    comb_clearance   comb to comb distance, should not be > (2 * tooth_width)
 *    base_height      comb base (optional), set to 0 to disable
 *    render_mode      0 ... all, 1 ... verification comb + base, 2 ... alignment comb
 *    extra_clearance  deprecated: extra clearance in case the comb pairs overlap (usually on small twidth and/or tgap)
 * 
 */

// Author : rubienr (https://github.com/rubienr)
// Source : https://github.com/rubienr/cad/blob/master/creality-ender-5-plus/printer-test-objects/nozzle-to-nozzle-offset-calibration-pattern/nozzle-to-nozzle-xy-offset-calibration-pattern.scad
// Origin : https://github.com/5axes/Calibration-Shapes/issues/15
// ------------------------------------------------------------------------------------------------------------------------

module drawComb (
    _num_teeth, 
    _teeth_gap,
    _tooth_width,
    _tooth_height,
    _tooth_length,
    _base_height,
    _render_mode) // 3 ... none, 4 ... bed only, 5 ... comb only, 6 ... all
{
  
  // base for better adhesion (optional)
  if (_base_height > 0 && (_render_mode == 4 || _render_mode == 6)) 
  {
    _comb_length = (_num_teeth - 1) * _teeth_gap + (_num_teeth + 2) * _tooth_width;
    _comb_width  =  _tooth_width + _tooth_length + 2 * _tooth_width;
    
    color("grey")
      translate ([-_tooth_width, -2*_tooth_width, 0])
        cube([_comb_length, _comb_width, _base_height]);
  }

  // comb
  if (_render_mode == 5 || _render_mode == 6) 
  {
    color_value = _render_mode == 1 ? "blue": (_render_mode == 2 ? "red" : "orange");
  
    // teeth
    for (t = [0:_num_teeth-1]) 
    {
      let (translation = [t * (_teeth_gap + _tooth_width), 0, _base_height])
      {
        translate (translation) color(color_value) cube ([_tooth_width, _tooth_length, _tooth_height], false);
        
        // center tooth mark
        if (t == (((_num_teeth - 1) / 2)))
        {
          translate (translation + [0, -_tooth_width, _tooth_height]) color(color_value) cube ([_tooth_width, _tooth_length / 2 + _tooth_width, _tooth_height]);
        }
      }
    }
    
    // comb back
    translate ([0, - _tooth_width, _base_height]) 
      color(color_value) 
        cube ([_num_teeth * _tooth_width + (_num_teeth - 1) * _teeth_gap, _tooth_width, _tooth_height], false);      
  }
}

// ------------------------------------------------------------------------------------------------------------------------

module drawCombPair(
    _teeth_count, 
    _teeth_gap,
    _tooth_width,
    _tooth_height,
    _tooth_length,
    _comb_clearance,
    _base_height,
    _render_mode) 
{
  _comb_displacement = [0, -_tooth_length - (_comb_clearance / 2), 0];
  _second_comb_teeth_displacement = _teeth_gap / ((_teeth_count - 1) / 2);
  _second_comb_teeth_gap = _teeth_gap + _second_comb_teeth_displacement;
  _second_comb_displacement = [-_teeth_gap, 0 , 0];

  // default comb
    translate(_comb_displacement)
      drawComb(_teeth_count, _teeth_gap, _tooth_width, _tooth_height, _tooth_length, _base_height,  
        _render_mode == 0 ? 6 :             // all
          (_render_mode == 2 ? 5 :          // comb only
            (_render_mode == 1 ? 4 : 3)));  // bed only

  // verification comb (stretched)
    mirror ([0,1,0]) 
      translate (_second_comb_displacement) // sync middle tooth with default comb 
        translate(_comb_displacement)
          drawComb(_teeth_count, _second_comb_teeth_gap, _tooth_width, _tooth_height, _tooth_length, _base_height, 
            _render_mode == 0 ? 6 :          // all
              (_render_mode == 1 ? 6 : 3));  // comb and bed
}

// ------------------------------------------------------------------------------------------------------------------------

module drawXYCalibrationCombs( 
    _teeth_count, 
    _teeth_gap,
    _tooth_width,
    _tooth_height,
    _tooth_length,
    _comb_clearance,
    _base_height,
    _render_mode,
    _extra_clearance) 
{
  _comb_width = _tooth_length + _tooth_width + _comb_clearance / 2;
  _t_x = [_comb_width + 2 * _tooth_width + _extra_clearance , 0, 0];
  _t_y = [0, -_comb_width + _tooth_width, 0];
  _r_y = [0, 0, 90];
  
  // X aligned comb pair
  translate(_t_x)
    drawCombPair(_teeth_count, _teeth_gap, _tooth_width, _tooth_height, _tooth_length, _comb_clearance, _base_height, _render_mode);

  // Y aligned comb pair
  translate(_t_y)
    rotate(_r_y) 
      drawCombPair(_teeth_count, _teeth_gap, _tooth_width, _tooth_height, _tooth_length, _comb_clearance, _base_height, _render_mode); 
}

// ------------------------------------------------------------------------------------------------------------------------

module draw()
{
  teeth_count    = is_undef(teeth_count)    ?  21 : teeth_count;     // number of teeth, recommended: 10 for positive offset + 10 for negative offset + 1 center = 21
  tooth_width    = is_undef(tooth_width)    ?   2 : tooth_width;     // width of one single tooth
  tooth_height   = is_undef(tooth_height)   ? 0.2 : tooth_height;    // height of teeth / comb, should be n * layer_height
  tooth_length   = is_undef(tooth_length)   ?  10 : tooth_length;    // length of one single tooth
  teeth_gap      = is_undef(teeth_gap)      ?   2 : teeth_gap;       // space in between teeth of the unscaled comb
  comb_clearance = is_undef(comb_clearance) ?   1 : comb_clearance;  // comb to comb distance, should not be > (2 * tooth_width)
  base_height    = is_undef(base_height)    ?   0 : base_height;     // comb base (optional), set to 0 to disable
  render_mode    = is_undef(render_mode)    ?   0 : render_mode;     // 0 ... all, 1 ... verification comb + base, 2 ... alignment comb; (>= 3 ... reserved for internal usage)
  
  // TODO rr - remove the need of the extra_clearance parameter: swap draw order (draw verification comb first, then align the default one)
  extra_clearance = is_undef(extra_clearance) ? 0 : extra_clearance; // extra clearance in case the comb pairs overlap (usually on small twidth and/or tgap)
  
  assert(teeth_count % 2 == 1, "An odd number of teeth is required.");
  drawXYCalibrationCombs(teeth_count, teeth_gap, tooth_width, tooth_height, tooth_length, comb_clearance, base_height, render_mode, extra_clearance);
}

// ------------------------------------------------------------------------------------------------------------------------
// Translate to center the part
translate([-44,-30.5,0]) draw();

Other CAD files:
CAD FIles/6_ Wafer Holder/[Final] 6- Wafer Holder (W- Tolerance, 8-31-23).step
CAD FIles/CNC Redesign/Bottom Plate VPD CNC v8/Sketch1.dxf
Ender 5 Cura Config/5.4/plugins/CalibrationShapes/CalibrationShapes/models/ParametricBedLevel.scad
CAD FIles/1mL Plastic Syringe Head v13/1mL Plastic Syringe Head_v13.3mf
CAD FIles/1mL Plastic Syringe Head v13/1mL Plastic Syringe Head_v13.f3d
CAD FIles/1mL Plastic Syringe Head v13/Syringe Head 1_f84ff1b6/Plunger Holder 1_a4f4313b/Plunger Holder.dxf
CAD FIles/1mL Plastic Syringe Head v13/Syringe Head 1_f84ff1b6/Plunger Holder 1_a4f4313b/Sketch4.dxf
CAD FIles/1mL Plastic Syringe Head v13/Syringe Head 1_f84ff1b6/Syringe Holder 1_7d3c671d/Holder Base.dxf
CAD FIles/1mL Plastic Syringe Head v13/Syringe Head 1_f84ff1b6/Syringe Holder 1_7d3c671d/Sketch10.dxf
CAD FIles/1mL Plastic Syringe Head v13/Syringe Head 1_f84ff1b6/Syringe Holder 1_7d3c671d/Sketch4.dxf
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

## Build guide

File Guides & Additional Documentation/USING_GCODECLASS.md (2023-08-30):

# A Guide To More In-Depth Code Modification Using `gCodeClass.py`

If you have not read the other code documentation, please do so ([README.md](/README.md), [CUSTOM_SCAN.md](CUSTOM_SCAN.md)).

This document discusses the structure, design, and usage of `gCodeClass.py` for more granular modificaitons to the scanning protocols than can be accomplished by only changing pre-existing paramaters and printer actions.

## Basic Structure
This section provides an overview of the function and design of the `gCodeClass.py` file.

The file is divided into two Python classes: `marlinPrinter` & `VPDScanner`. Since the VPD scanner is an abstraction of the functions available on a consumer 3D printer, it was useful to split the functions available into these two categories.

The `VPDScanner`is the child class of `marlinPrinter`, inheriting its functions and parameters.

1. ### `marlinPrinter` Class

- The `marlinPrinter` class contains an assortment of G-Code commands that are useful for the purposes of this project. By containing all of these functions within a class (as opposed to regular functions in a Python script), we are able to attach the G-Code commands to the class object instead, which eliminates the need to write to a file after every command or to pass around a list of commands from function to function.

    1. ### `coords` / Coordinates Dictionary 
        1. #### Structure
            - Most of the functions use coords argument, which is formatted as a dictionary with the axis as the key and value for each respective axis (ex `coords = {'X': 10.0, 'F': 1000, 'E': 0.1}`)
            - There are multiple reasons to use a dictionary instead of a `math` vector object or list. Using a dictionary allows for a combination of verbosity and concision that is appealing for enhancing readibility of the code.
                - Since the object is a dictionary, only the axes used need to be defined. This eliminates the need to contain unnecesary `None` or `0` values for unused axes, which would be neccesary in a string or vector.
                - However, each axis does have to be defined for each call of the `coords` value. This decision means the code is more readable for someone unfamiliar with the program, as well as reducing the likelihood of errors. 
                    - Consider the difference between `[0.105, None, None, 1]` and `{'E': 0.105, 'X': 1}`. In the latter example it is clear which value is assigned to each axis.
        2. #### `@sanitizeCoords` Wrapper
            - To minimize the likelihood of errors, a wrapper function was written which controls the style and formatting of `coords ` variables passed into functions. `@sanitizeCoords` accomplishes three main functions.
                1. `addDecimalPoint`
                    - Since G-code can sometimes have issues if commands are passed in without decimal points (such as 3 instea of 3.0), this function adds a decimal point to all values.
                2. `adjsutForOffset`
                    - Since the new scanhead is in a different point in space from the original printhead, the same movement command will make the syringe tip move to a different point in space. We still want the printhead to move to the defined point, so we calculate and/or measure the offset by using a known reference point or by referencing CAD.
                3. `limitDecimalPlaces`
                    - Although we want decimal points in all commands, we do not want exess decimal points. The system has a limited amount of granularity in space (it can only move in a limited interval). Thus providing too many decimal places can cause errors too, so this function limits decimal places to 4.
            - **Cases when we do not want to account for head offset:** 
                - Sometimes accounting for the head offset can cause issues in the code.
                    1. For example, adjusting for the head offset when scanning the wafer will cause issues. Since the rotation move in G-code is defined by the printhead's relative position to the circle's center, adjusting for the printhead on every rotation will cause a gradual shift in the location of the circle's center.
                    2.  When using the Cuevette, we want to use absolute coordinates, not coordinates adjusted for the printhead. Since the location of the cuevette is determined experimentally, adjusting for the head offset will make the printhead go to the wrong point in space.
                - `undoHeadOffset` will correct for this issue. Make sure to be careful where and when you adjust for the new printhead.

2. ### `VPDScanner` Class

    - As noted earlier, this class inherits (is a child class of) the `marlinPrinter` class. Functions in this class are either specifically for the scanner or build on & combine simple G-code functions to create a movemement pattern specifically suited for VPD scanning.

    - Most functions are self-explanatory and documented sufficiently within the code. This section will highlight any particularly confusing portions of this class.

    1. ### `calcEFeedRate`
        - This function allows for easy changes of the syringe used for the scan droplet. Since the 'E' paramater of the `coords` dict is in mL, some calculations must be done to calculate how much the motor must move per mL. This function accomplishes that task. The printer is told of this value in the start G-code.
    2. ### `doWaferScan`
        - This function is designed to scan a wafer of specified size. Since it is a complicated series of actions, this section walks through each of those steps sequentally.
            1. Calculate the `max_radius `and `max_rotations`.
                - The max radius is the given radius of the wafer without the `EDGE_GAP`, to ensure that the syringe doesnt hit the edges and that the drop does not fall off of the wafer.
                - The max rotations are calculated by dividing the max radius by the droplet size, and taking the lowest integer value of the quotient, eliminating any bugs resulting from partial scan arcs from decimals.
            2. Center the printhead, move the printhead to the scanning height.
            3. Move to the max radius, dispense solution.
            4. While loop: scanning arcs.
                - For each rotation, the printhead will move to the radius of the scan arc. The program then calculates the position of the center of the wafer relative to the printhead (neccesary for G-code arcs), and executes a circular move.
                - After the move is completed, the program increases the `rotation_count` until the maximum rotations are reached.
            5. Pick up the scan droplet.
                - Since the scan droplet tends to trail behind the syringe nozzle, this section does a counter clockwise rotation backwards while pulling the syringe plunger up. This is in an attempt to recover as much of the drop as possible.

## Making & Modifying Functions

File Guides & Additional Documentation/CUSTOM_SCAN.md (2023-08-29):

# Creating Custom Scan Routines
**For all modifications, use `TEMPLATE.py`, as this file contains the framework needed to make basic modifications to the scanning routine.**

-----
The VPD scanning program has been written with the intention of being easy to change for anyone with minimal programming experience. The types of modifications that can be made can be broken down into three subcategories:
1. Instance Parameters
2. Class parameters
3. Actions

This document outlines how (and when) to make these modifications. 

| Category                | Sub-category / Parameter             | Description |
|-------------------------|-------------------------------------|-------------|
| **Instance Parameters** | marlinPrinter: `filename`            | Filename to which gcode commands are written. Can have .gcode extension or not. |
|                         | VPDScanner: `sample_volume`          | Determines the droplet volume for scanning the wafer. |
| **Class Parameters**    | **Printer Parameters**              |             |
|                         | *_OFFSET Parameters*                | Specify offsets for printer to compensate for non-standard printhead. Parameters include `X_OFFSET`, `Y_OFFSET`, `Z_OFFSET`. |
|                         | *_MAX Parameters*                   | Specify the maximum print space dimensions. Includes `marlinPrinter.X_MAX`, `marlinPrinter.Y_MAX`, `marlinPrinter.Z_MAX`. |
|                         | **Scanner Parameters**              |             |
|                         | *Motor Speeds (Feedrate)*          | Determine speed of movement. Parameters are `VPDScanner.TRAVEL_FEEDRATE`, `VPDScanner.SCANNING_MOVE_FEEDRATE`, and `VPDScanner.EXTRUSION_MOTOR_FEEDRATE`. |
|                         | *Heights*                           | Parameters are `VPDScanner.SCAN_HEIGHT` and `VPDScanner.TRAVEL_HEIGHT`. |
|                         | *Cuevette Info*                     | Specifies deepest point syringe should reach in cuevette. Parameters are `CUEVETTE_X`, `CUEVETTE_Y`, and `CUEVETTE_Z`. |
|                         | *Wafer Variables*                   | Parameters related to wafer being scanned include `VPDScanner.WAFER_DIAM`, `VPDScanner.EDGE_GAP`, and `VPDScanner.DROPLET_DIAMETER`. |
|                         | *Scan Head Variables*               | Parameters related to physical scan head. Includes `SYRINGE_CAPACITY`, `SYRINGE_LENGTH`, `RACK_TEETH_PER_CM`, and `GEAR_TEETH`. |
| **Actions**             | scanner.loadSyringe() / scanner.unloadSyringe() | Manually load or unload syringe. |
|                         | scanner.doWaferScan()               | Scan area of specified wafer, center head, calculate and execute scan rings. |
|                         | scanner.useCuevette(dispense = TRUE/FALSE) | Use cuevette either as reservoir or sample holder based on `dispense` argument. |

## Instance Parameters
Instance paramaters **must** be provided when creating an instance of a class. The two classes in this project are *marlinPrinter* & *VPDScanner*. Each class has one parater that must be supplied when creating an instance.

While there is no technical reason for the separation of instance & class parameters, the separation between the two is meant to convey how often one should change the parameter. Instance parameters should be changed easily & freely without concern. Class paramaters should be changed more thoughtfully.

#### marlinPrinter: `filename`
- The filename argument must always be passed to a marlinPrinter. This filename is where the gcode commands will be written, always in the local directory. The name can either have *.gcode* or not, as there is handling in place for both cases.

#### VPDScanner: `sample_volume`
- This parameter tells the program how large of a droplet should be used to scan the wafer.

## Class Parameters
**NOTE: In order to change class parameters, the `changeDefaultParams(scanner)` function must be called at the start of the scan routine. Then the appropriate variable should be uncommented and changed.**  

*ALL PARAMATERS ARE IN **mm** AND **mL** UNLESS OTHERWISE SPECIFIED.*

1. ### Printer Parameters
    1. #### *_OFFSET Parameters*
        - **Only modify these parameters if the physical printhead changes.** These parameters have been tuned for the given printhead and syringe.

        - The offset paramaters (`X_OFFSET`, `Y_OFFSET`, `Z_OFFSET`) tell the printer how far off the printehead is from the regular Ender 3 printhead. Thus, when the command to go to the center of the bed is written, the syringe nozzle actually goes to the center, instead of the old printhead being centered on the buildplate.

    2. #### *_MAX Parameters*
        - The _MAX paramaters should be modified if the printer being used is not the Ender 3. These paramaters tell the program how large the printspace is, and this were the center of the print surface is.

        - `marlinPrinter.X_MAX`, `marlinPrinter.Y_MAX`, `marlinPrinter.Z_MAX`, all specify the maximum distance that can be travelled in one direction.

        - **NOTE:** The XY paramaters are not the usable printspace (which you may find searching online). Instead, they are the measured lengths of the buildplate. This is used so that the printhead centers itself on the center of the wafer.

2. ### Scanner parameters
    1. #### *Motor Speeds (Feedrate)*
        - This category includes:
            - `VPDScanner.TRAVEL_FEEDRATE`
            - `VPDScanner.SCANNING_MOVE_FEEDRATE`
            - `VPDScanner.EXTRUSION_MOTOR_FEEDRATE`
                - **NOTE:** Be particularly careful modifying the extrusion motor feedrate, especially after changing the gears. The issue is specifically with too high feedrates, as they can chew up gears, damage the syringe, etc.

        - Feedrate measures how fast an axis should move, in units of mm/s. If you would like the axes to move faster, increase the value. To decrease speed, decrease the value. See above note for the extrusion motor feedrate.

    2. #### *Heights*
        - `VPDScanner.SCAN_HEIGHT`
            - This value (in mm) changes the height of the syringe tip while scanning. If the drop is falling off or if the syringe is grinding into the wafer, this variable should be changed accordingly
        - `VPDScanner.TRAVEL_HEIGHT`
            - Changes the height of the printhead when making large travel moves. **ENSURE that this height is high enough so that the printer will not run into the cuevette holder or any other obstructions.

    3. #### *Cuevette Info*
        - These three variables (`CUEVETTE_X`, `CUEVETTE_Y`, `CUEVETTE_Z`) specify the location of the deepest point the syringe head should reach in to the cuevette to load/unload samples.

4. ### *Wafer Variables*
    - These variables specificy what wafer is being scanned and how to scan it.
        - `VPDScanner.WAFER_DIAM`
            - The diameter of the wafer being scanned in mm.
        - `VPDScanner.EDGE_GAP`
            - Since wafers have flats along the edges, the scanner does not scan the entire surface of the wafer, instead offsetting the first scan ring from the edge of the wafer. This parameter determines the length of that gap.
        - `VPDScanner.DROPLET_DIAMETER`
            - The size of the scan drop on the wafer. By using the wafer diameter and edge gap, the program automatically calculates the amount of scan rings neccesary. Smaller drop diameter will mean there are more scan rings, vice versa.

4. ### *Scan Head Variables*
    - In general these variables **should not** be changed unless the physical scan head is changed.
    - `SYRINGE_CAPACITY` & `SYRINGE_LENGTH`
        - The capacity (mL) and length of that capacity (mm) of the syringe used. This allows the system to determine how far to move to dispense or collect a specific volume from the syringe.
    - `RACK_TEETH_PER_CM` & `GEAR_TEETH`
        - Using the above syringe variables, the system can calculate the motor distance needed for specific volume extrusion moves. 

## Actions
In addition to changing *how* and *where* the scanner scans through parameters, you can also change *what* the scanner does during it's scan routine.

This sections the main actions that can be called during a VPD scanner's scan routine.

1. ### `scanner.loadSyringe()` / `scanner.unloadSyringe()`
    - These routines allow you to manually load or unload the syringe before or after the scan routine as appropriate.

    - `scanner.loadSyringe()`
        - This function moves the syringe to the origin and travel height, and opens the plunger holder to the appropriate height for the specified *sample_volume*.
        - **NOTE:** For this function to work properly, the plunger holder should be at the "0mL" mark on your syringe *before* starting the program. Since printers do not know nay absolute coordinates, and only know how to move relative to where they were, this function will move the plunger to the wrong location if the routine is not started at 0mL on the plunger holder.
    - `scanner.unloadSyringe()`
        - Moves the printhead to the origin and travel height, opening the 

2. ### `scanner.doWaferScan()`
    - This routine can be called to scan the appropriate area of any speified wafer. It will center the head, calculate the neccesary scan rings, and execute them. Then, it will collect the drop back up by doing a sweep backwards to pick up the tail of the drop.

3. ### `scanner.useCuevette(dispense = TRUE/FALSE)`
    - This routine uses the cuevette as either a reservoir or sample holder depending on how the `dispense` argument is specified
        - `dispense = TRUE`
            - This dispenses the collected droplet from the wafer into the cuevette.
        - `dispense = FALSE`
            - Uses the cuevette as a fluid reservoir, withdrawing up `sample_volume` mL of fluid.

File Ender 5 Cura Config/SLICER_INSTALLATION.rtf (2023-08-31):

To install the custom tuned printer parameters, install “Cura” (made by Ultimaker) from their website. Make sure to use version 5.4 or newer.

Once installed, navigate to Help > show configuration folder

Replace the contents of that folder with the contents of the folder “5.4.” You should be all set up!

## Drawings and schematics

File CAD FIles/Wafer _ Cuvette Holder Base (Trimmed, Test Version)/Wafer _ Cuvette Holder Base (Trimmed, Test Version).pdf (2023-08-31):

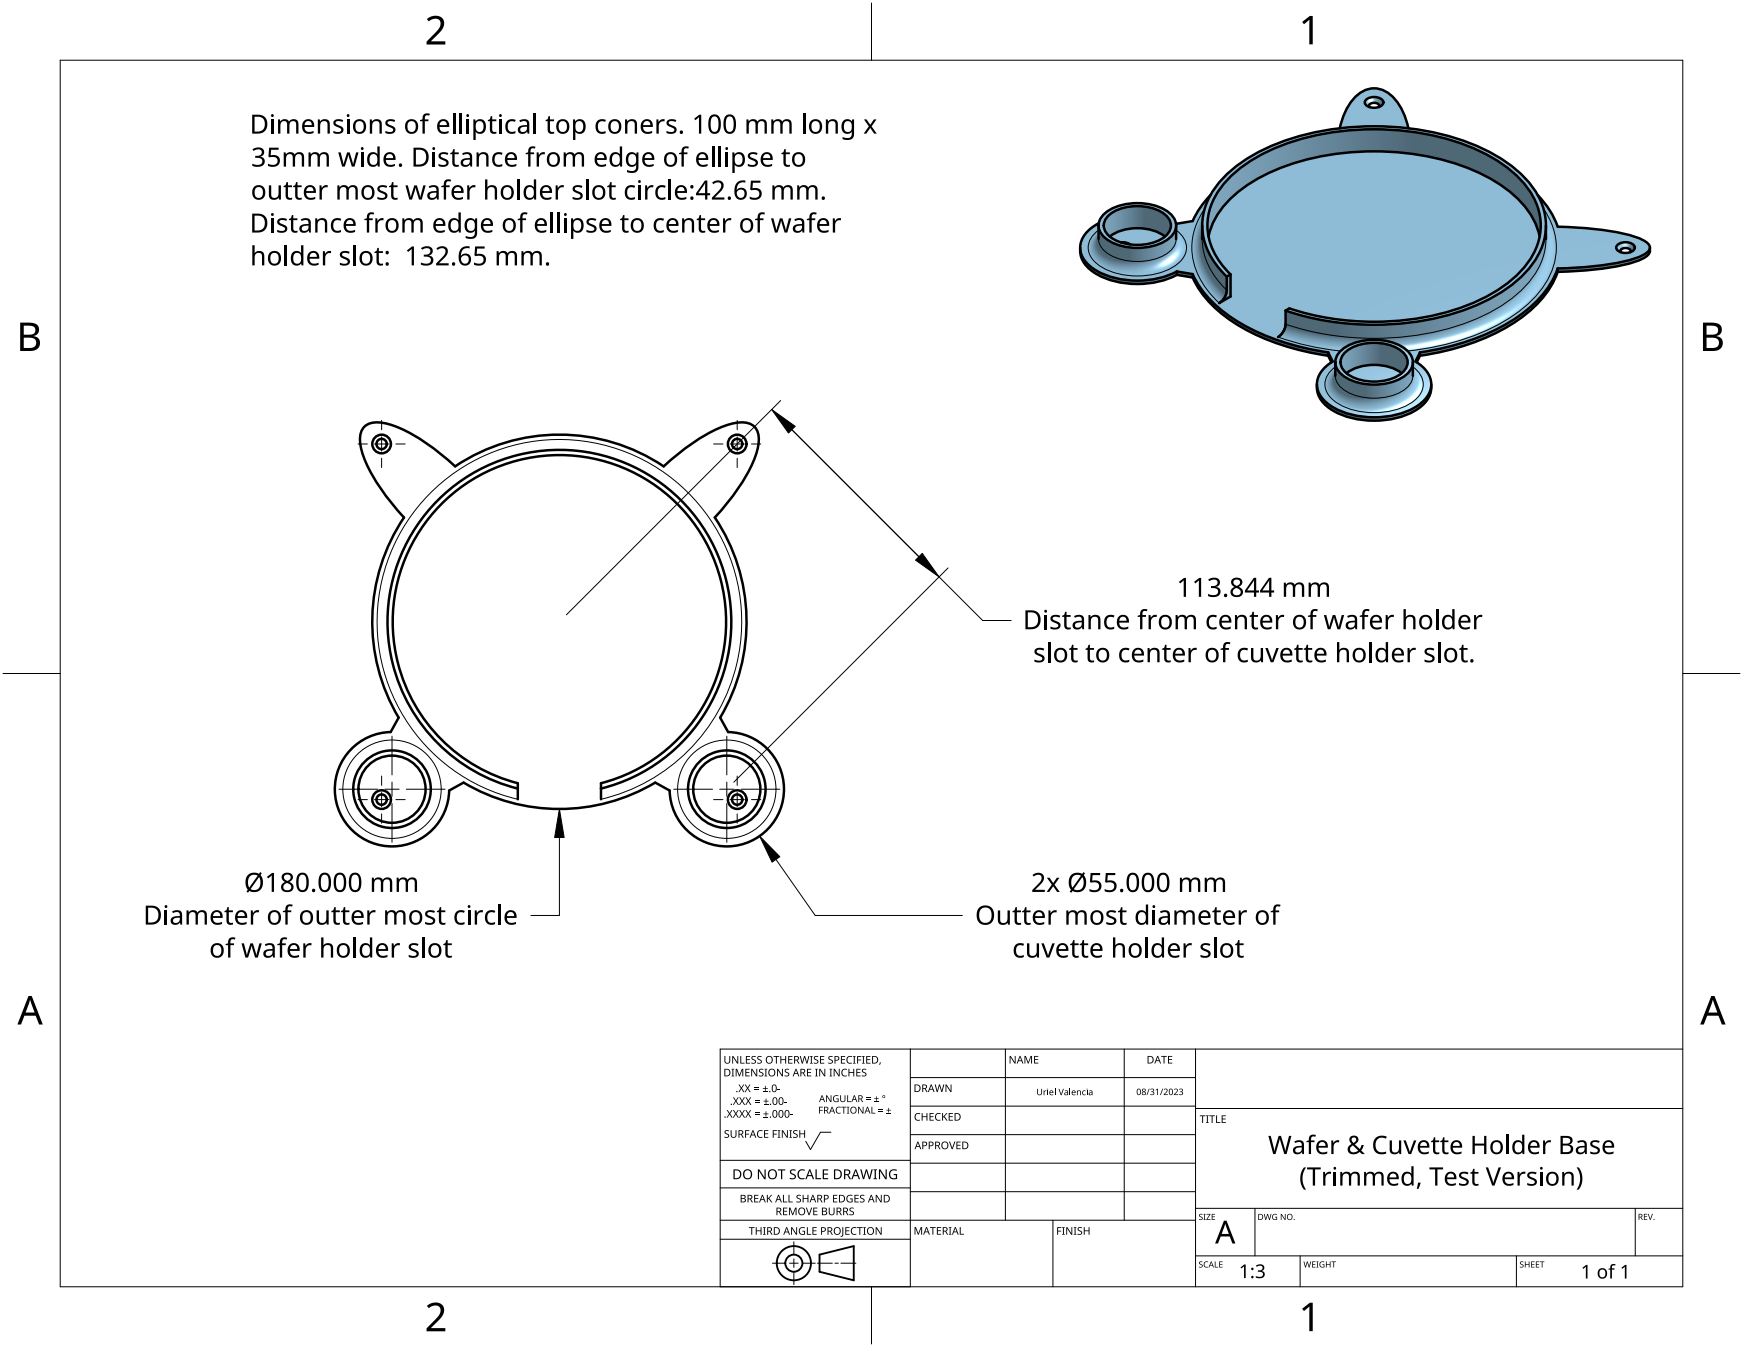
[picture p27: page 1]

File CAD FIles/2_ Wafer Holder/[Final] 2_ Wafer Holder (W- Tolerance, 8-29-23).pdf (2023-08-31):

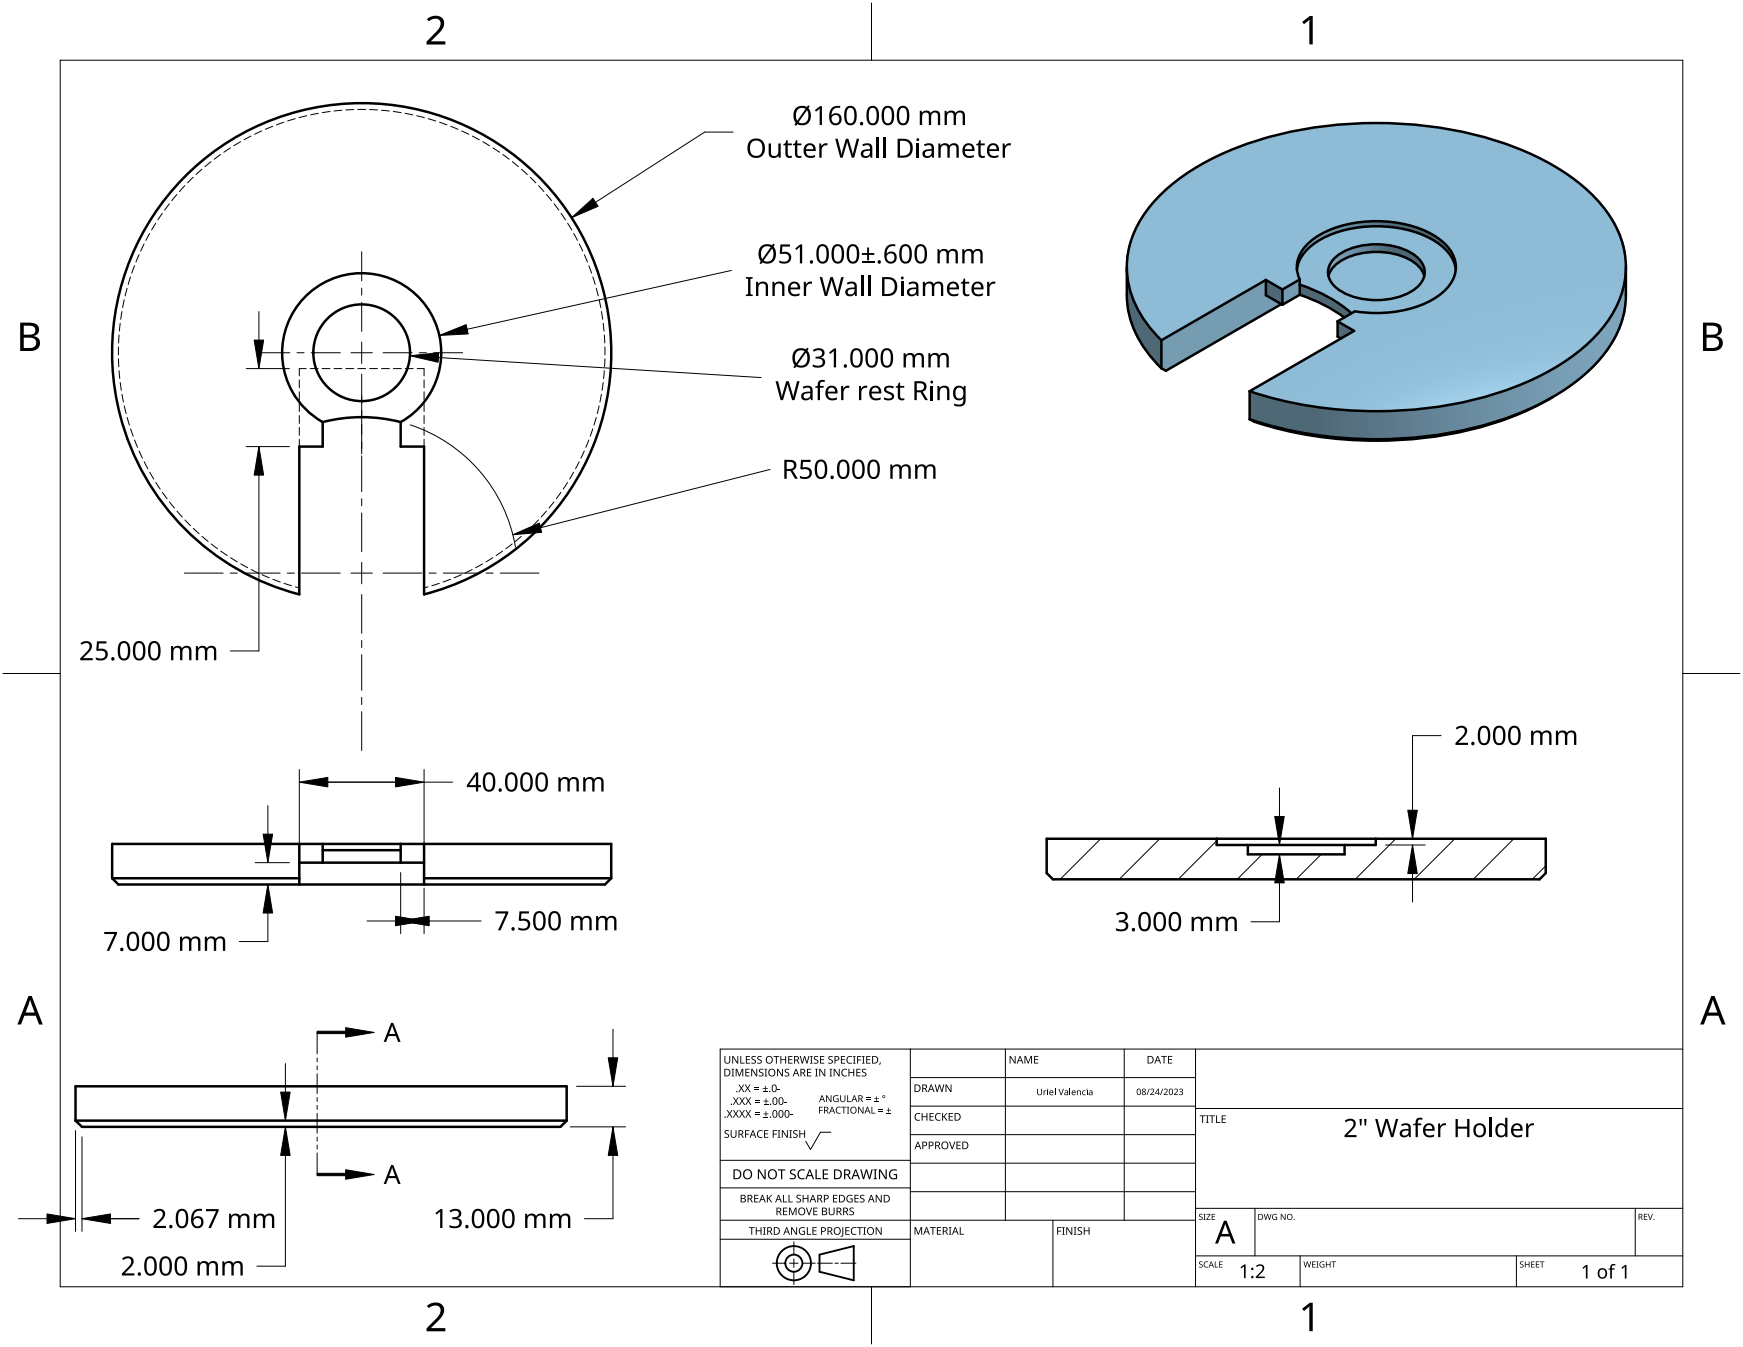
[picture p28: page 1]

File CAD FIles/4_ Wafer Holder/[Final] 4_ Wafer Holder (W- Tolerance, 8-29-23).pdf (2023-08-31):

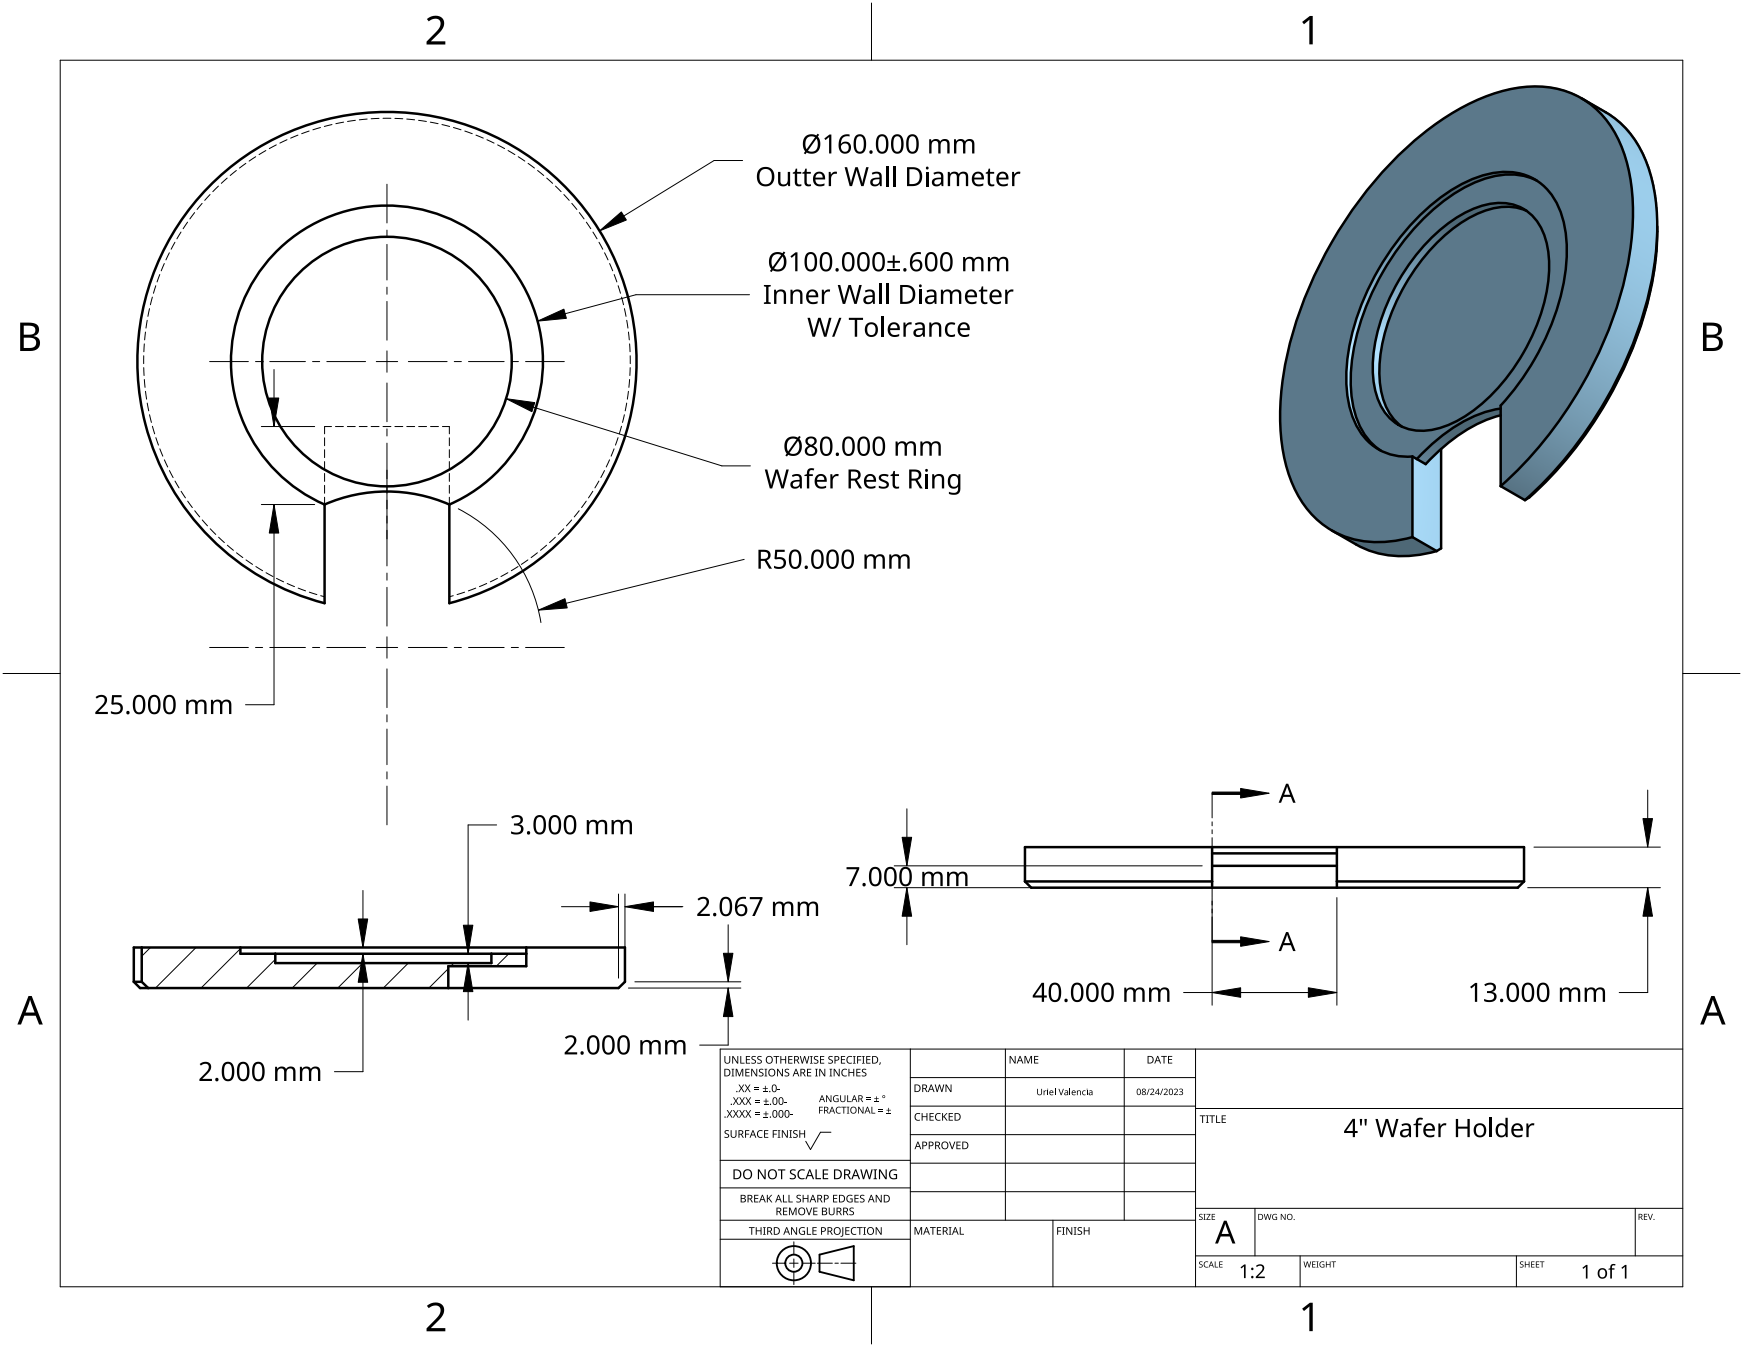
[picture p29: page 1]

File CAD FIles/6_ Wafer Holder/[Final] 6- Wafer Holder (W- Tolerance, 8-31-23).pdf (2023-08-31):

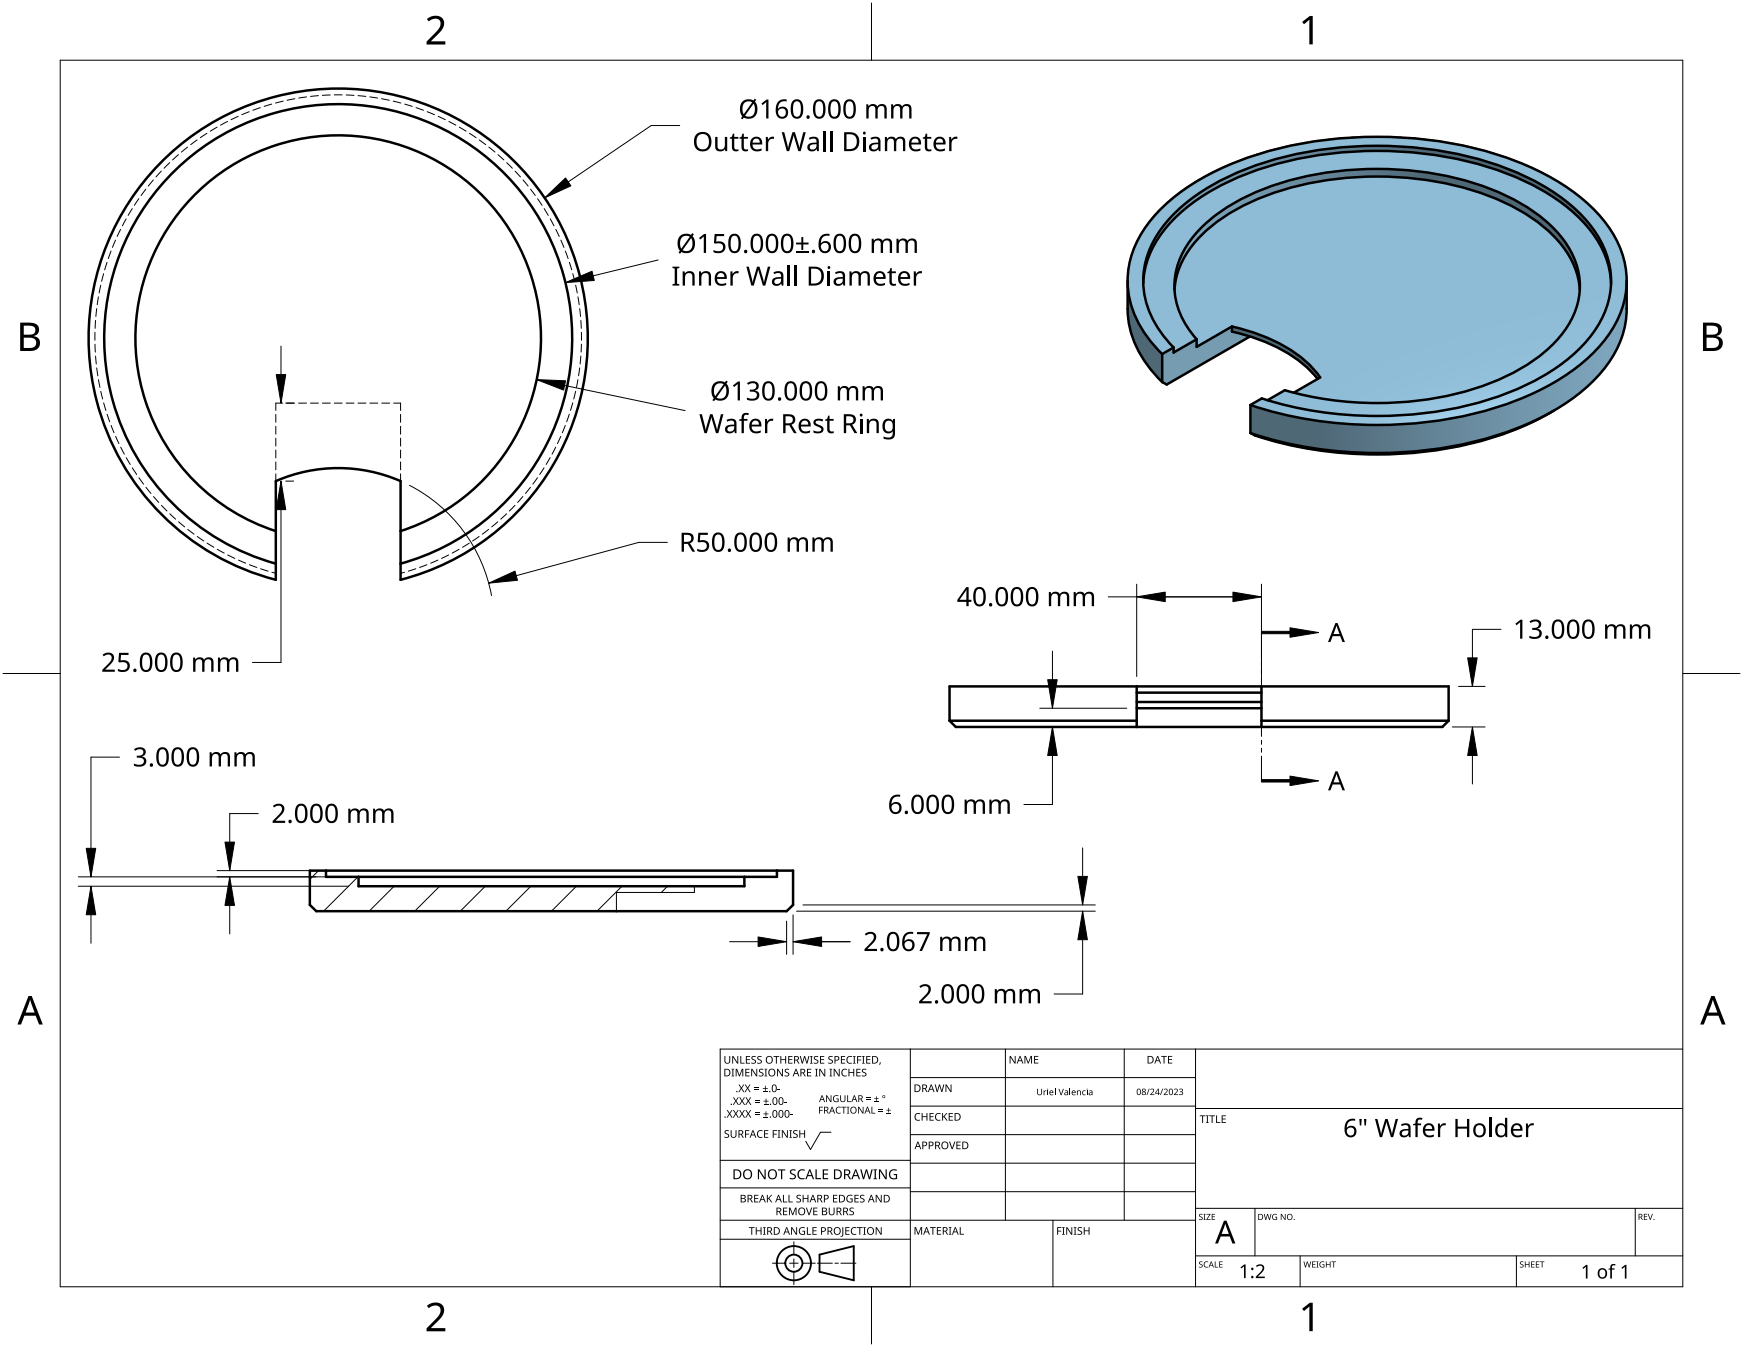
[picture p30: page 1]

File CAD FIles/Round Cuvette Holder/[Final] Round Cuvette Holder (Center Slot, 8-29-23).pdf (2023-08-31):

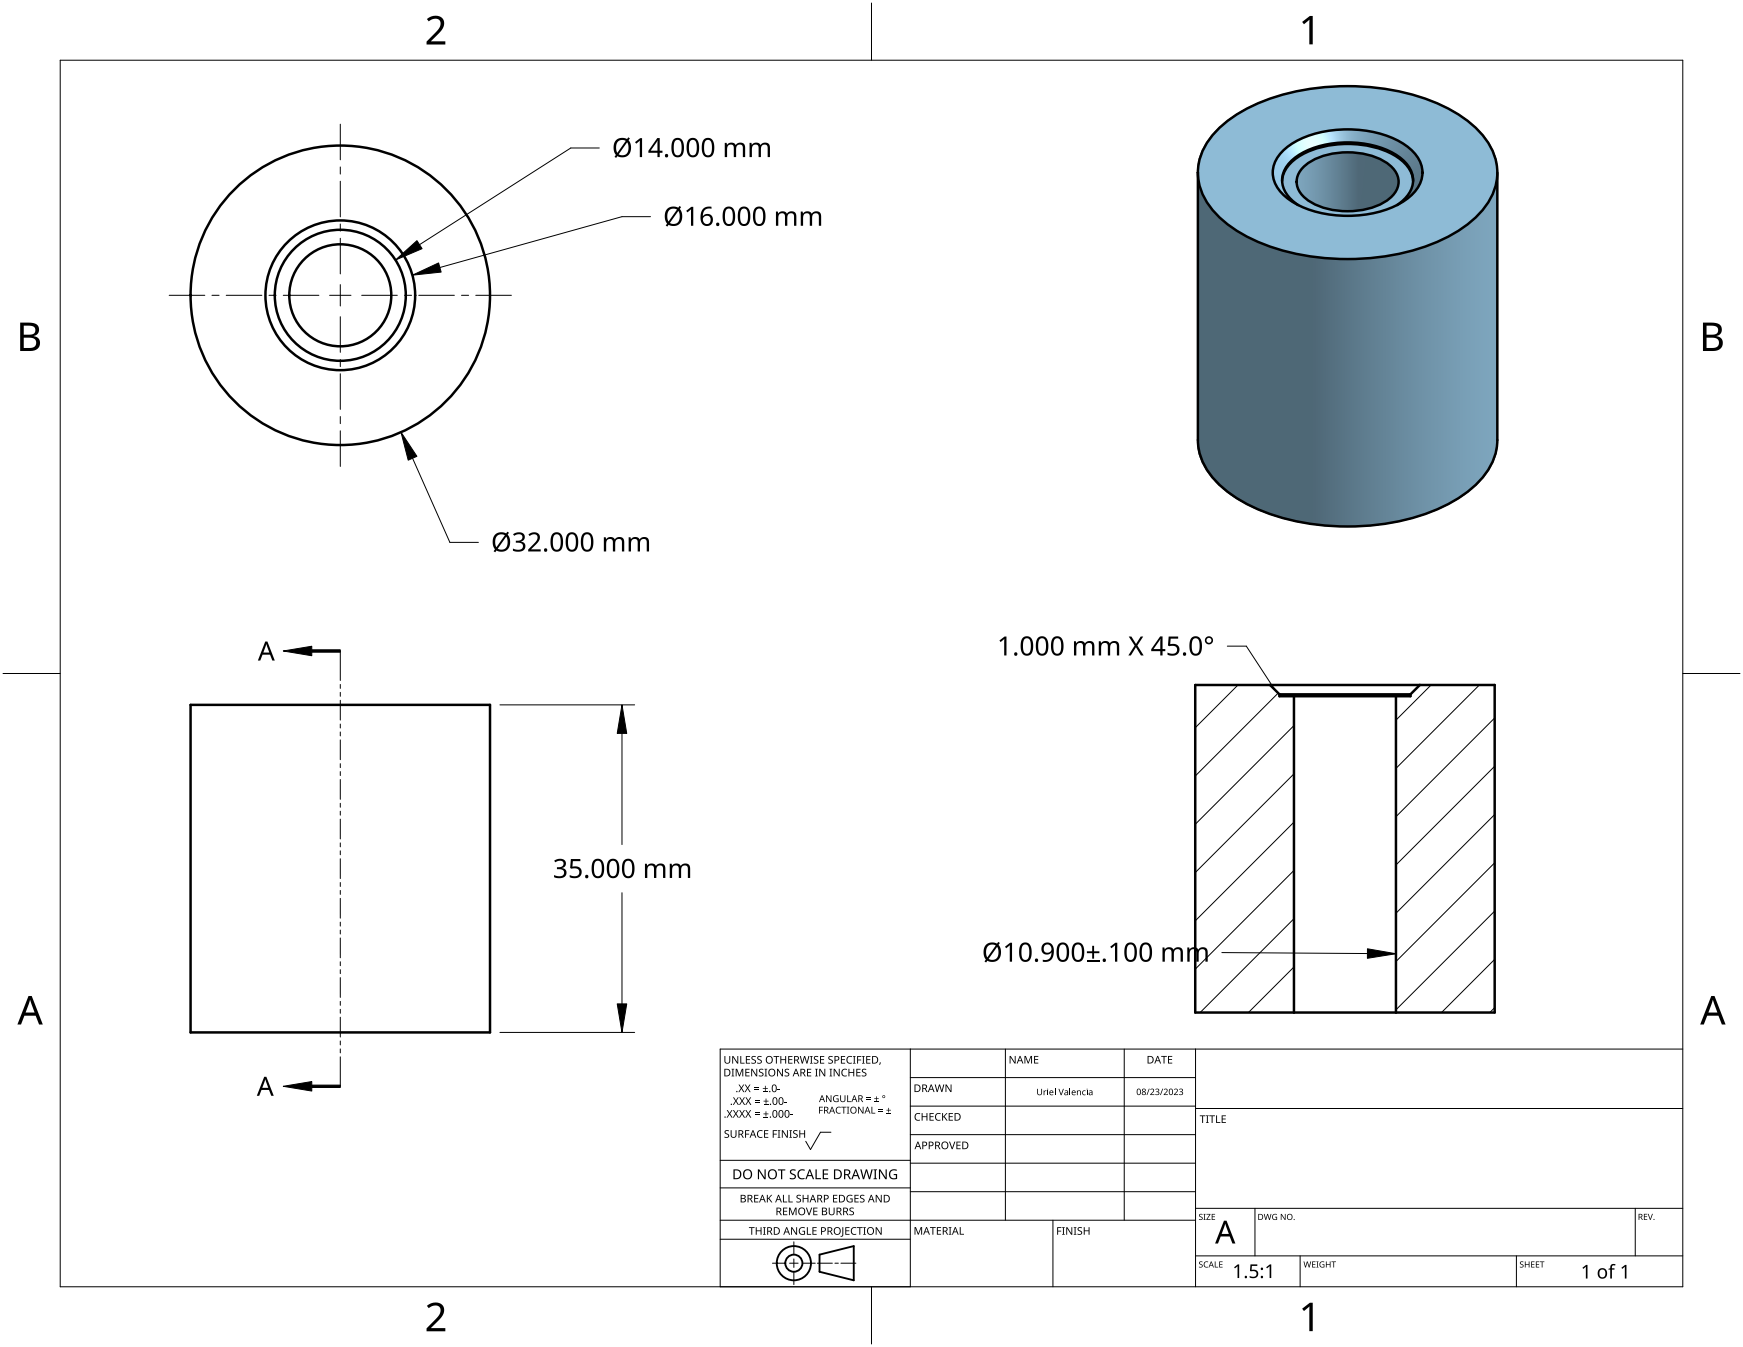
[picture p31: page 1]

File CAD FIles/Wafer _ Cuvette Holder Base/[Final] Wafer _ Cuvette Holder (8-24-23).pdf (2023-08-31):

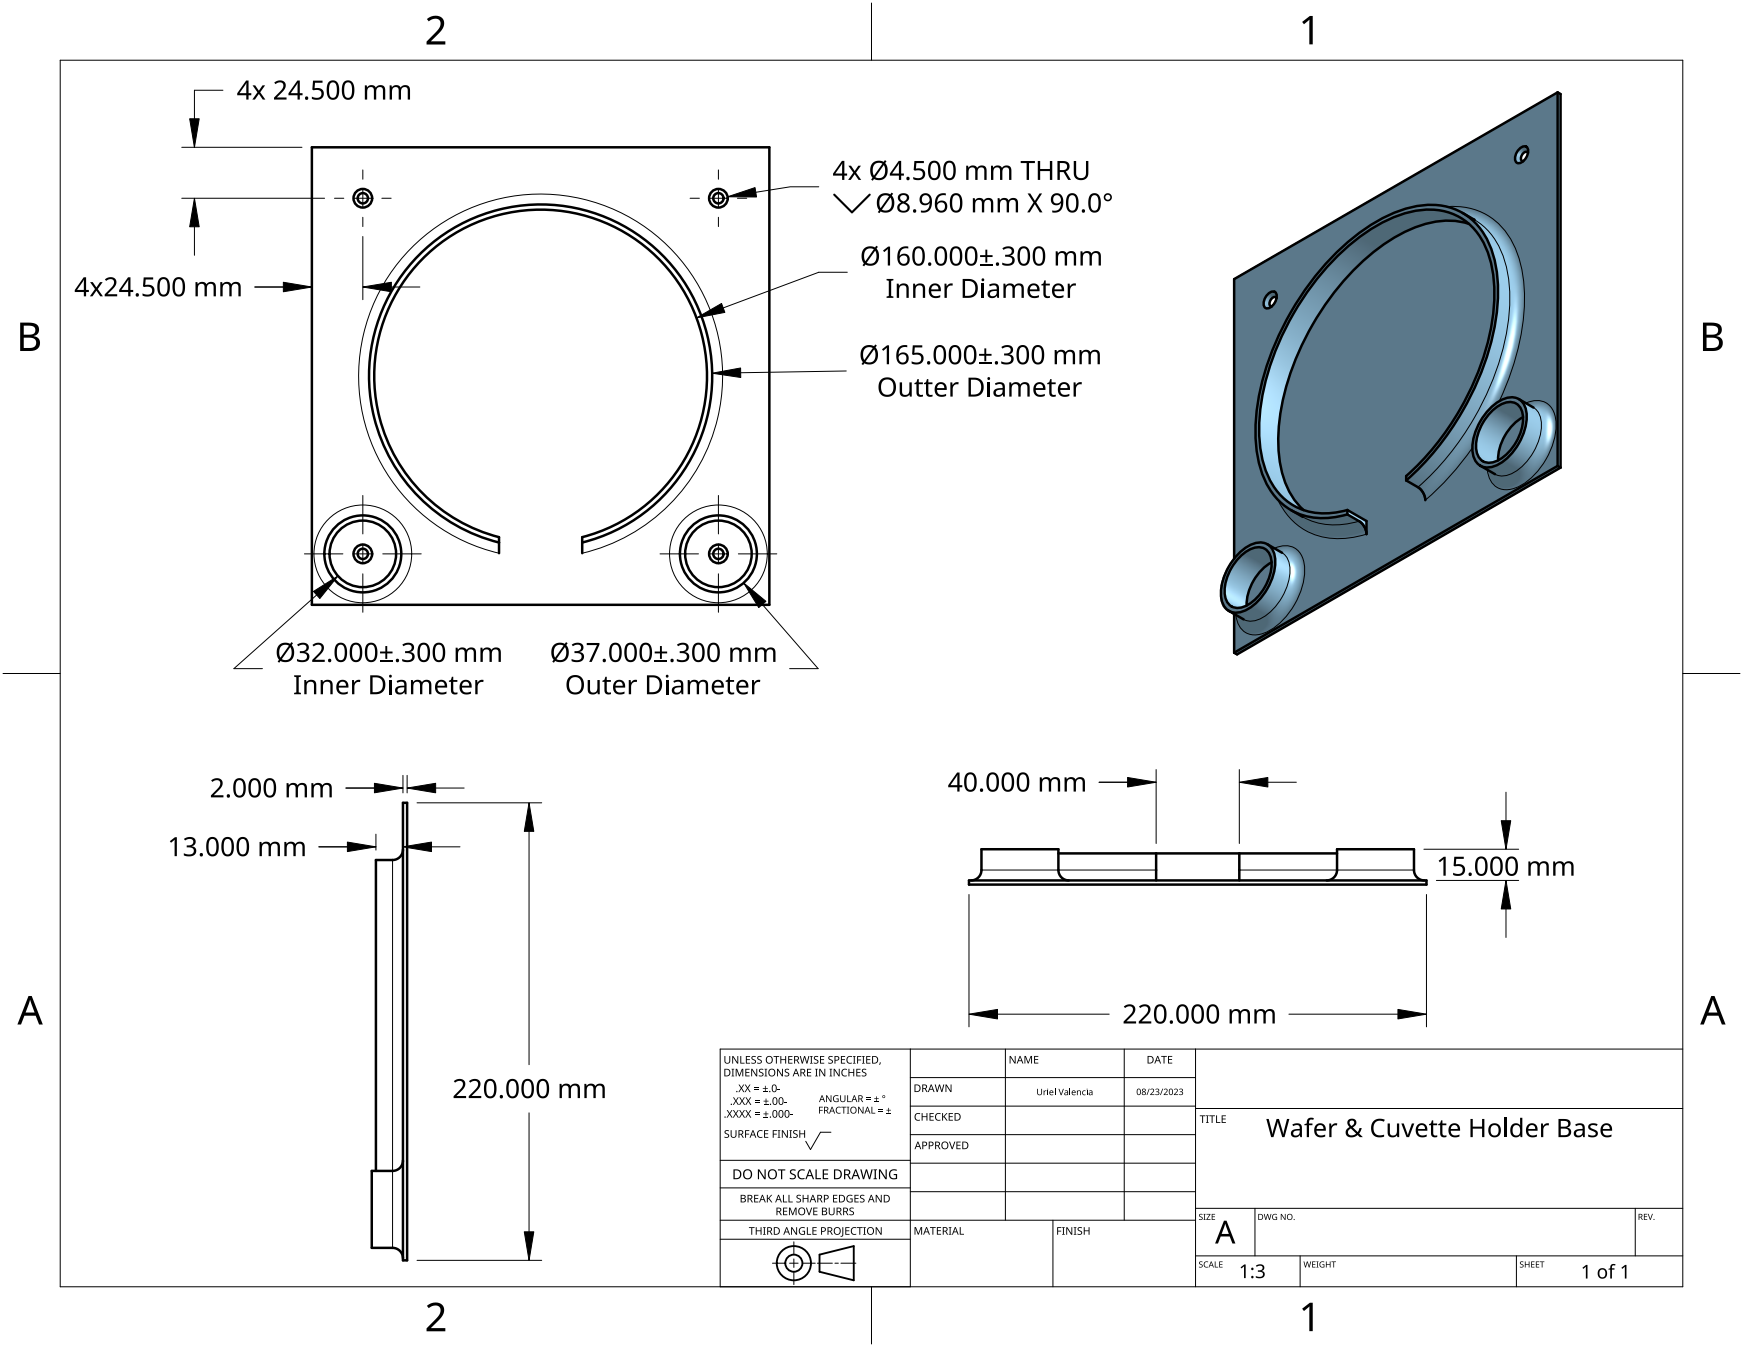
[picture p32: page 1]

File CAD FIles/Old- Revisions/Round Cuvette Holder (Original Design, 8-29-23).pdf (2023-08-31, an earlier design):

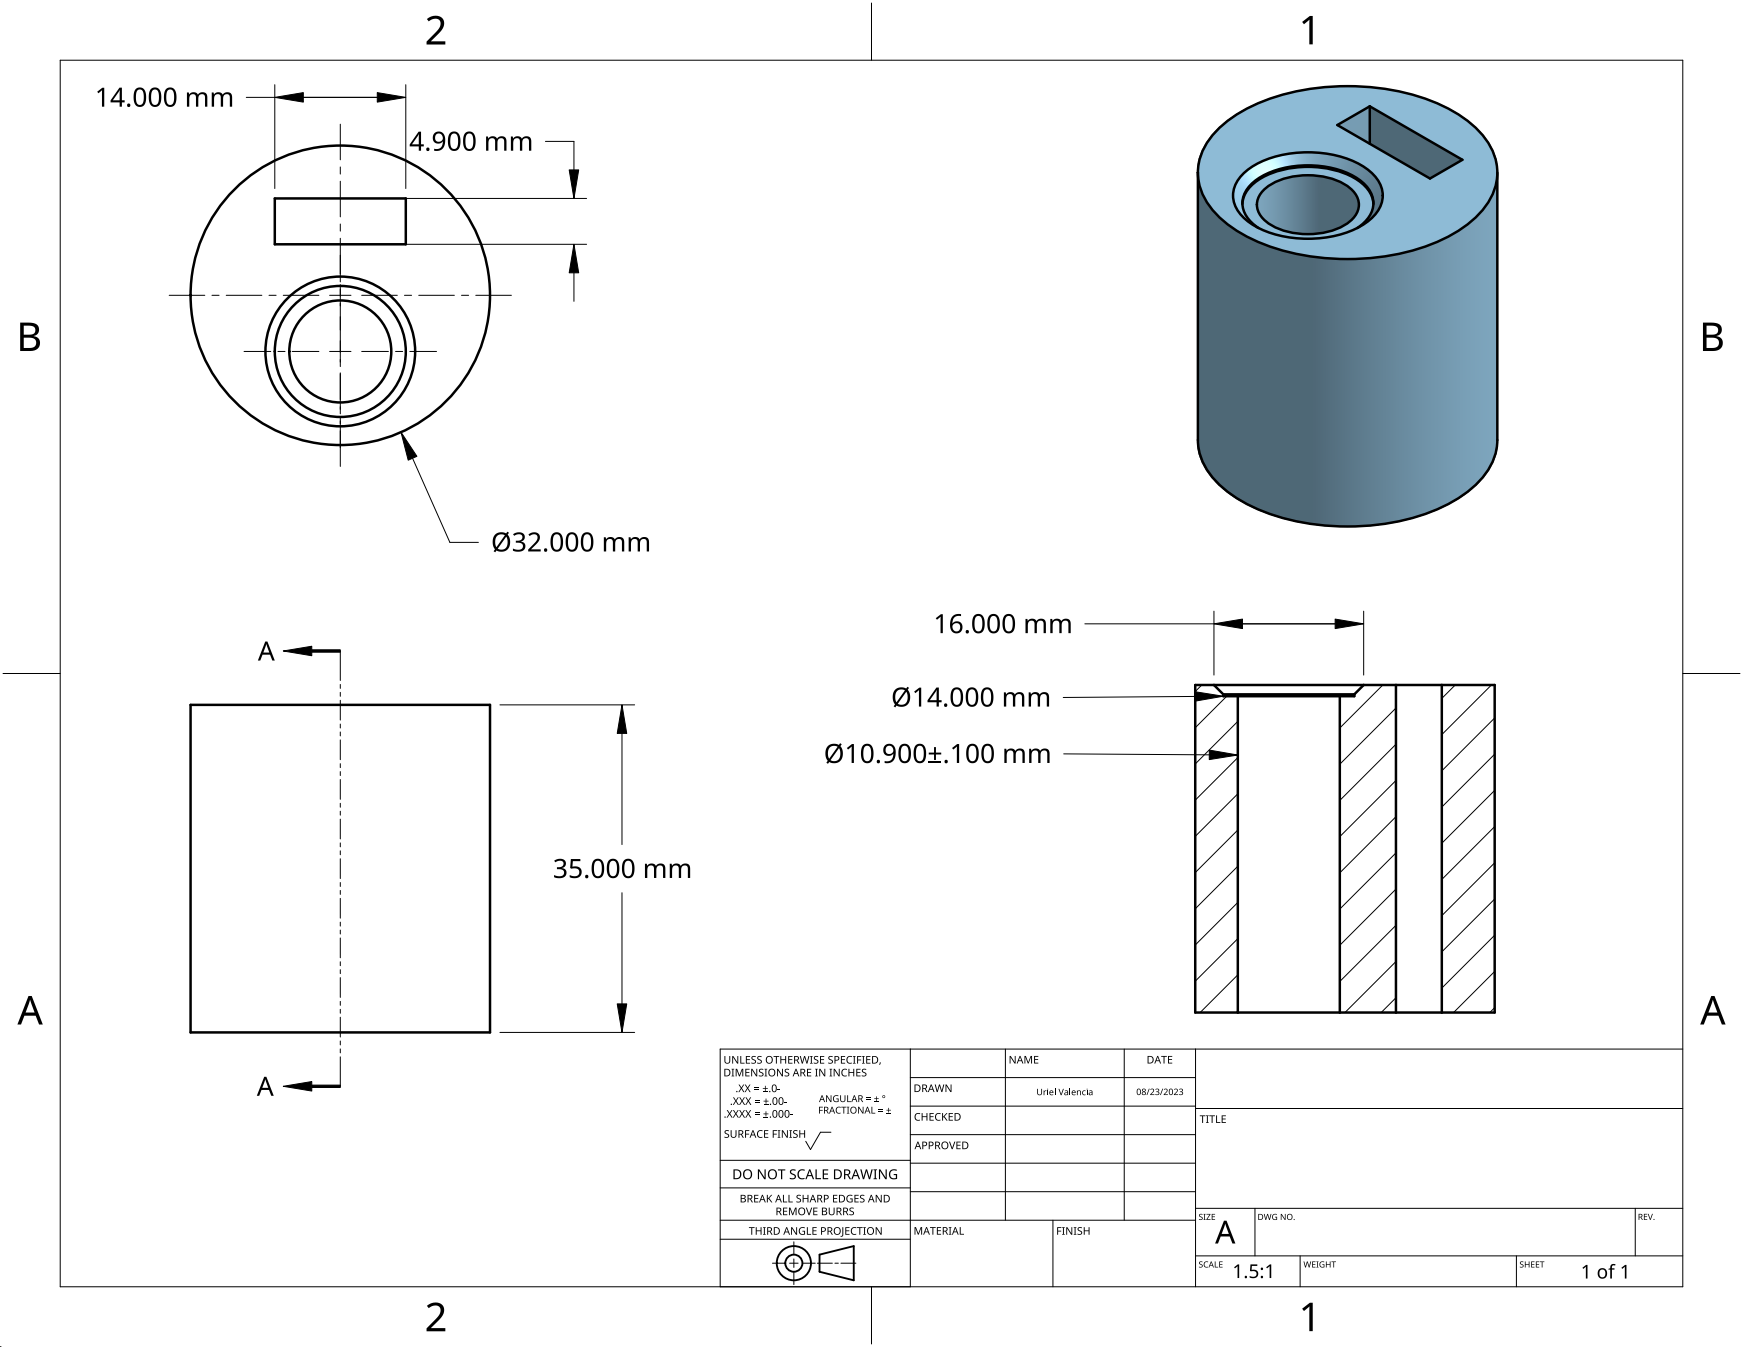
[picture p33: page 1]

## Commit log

2023-08-03 Added basic dispense sample custom command
2023-08-15 Added a way to change parameters of printing code
2023-08-15 Added print build volume to class variables.
2023-08-17 Differentiated between syringe capacity & sample volume
2023-08-21 Began testing with printhead for new plastic 3mL syringe
2023-08-23 Modified parameters for actual installed syringe head
2023-08-30 Added files for testing scan paramaters
    levelScanner -- protocol for leveling the syringe nozzle for even scanning
    scanHeightTester -- cycles through a range (user changeable) of scan heights to decide which is optimal
    scanVolumeTester -- similar to scanHeightTester, cycles through many scan volumes so that the user may choose which is optimal for their use case
2023-08-31 Added suite of testing files for narrowing in scan parameters
    - Level scanner helps level the syringe nozzle relative to the wafer holder (4in)
    - longevityTester tests the lifespan of the pinion gear
    - scanHeightTester repeats a single scan ring at a variable range of heights of your choosing
    - scanVolumeTester is similar to scanHeightTester, it does a ring with various volumes (specified in program, start, interval, range). Prompts user to change volume at every switch.
2023-08-31 Added Fusion 360 CAD Files
    [12-Piece Set Stainless Steel Dispensing Needle with Luer Lock Connection_v2.3mf, 12-Piece Set Stainless Steel Dispensing Needle with Luer Lock Connection_v2.f3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]
2023-08-31 Added scan radius command line printouts when function is run.
2023-08-31 Added config files for Ender 5 Cura profile & settings
    [AccelerationTower.scad, AccelerationTower.stl, Bed Level Pattern - Concentric Squares 150x150.stl, Bed Level Pattern - Concentric Squares 180x180.stl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]
2023-08-31 Added Uri's CAD files & documentation
    [12-Piece Set Stainless Steel Dispensing Needle with Luer Lock Connection_v2.3mf, 12-Piece Set Stainless Steel Dispensing Needle with Luer Lock Connection_v2.f3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]
